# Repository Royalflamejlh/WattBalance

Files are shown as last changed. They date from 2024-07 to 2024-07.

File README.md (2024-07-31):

# ECE445-Wattbalance

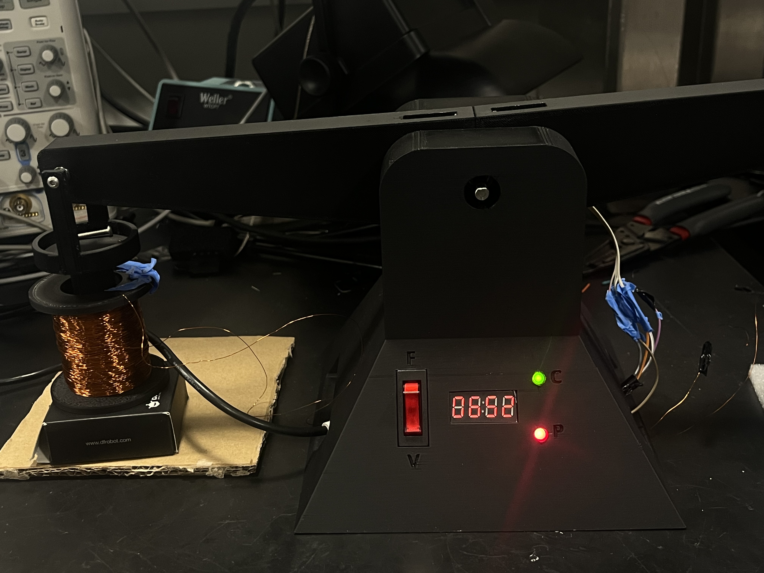
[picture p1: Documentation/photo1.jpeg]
Watt Balance


## Introduction
Our senior design project focused on the development of a Kibble balance, also known as a watt balance. This is an instrument capable of precise measurements based on electromagnetic forces and the definition of a kilogram based on fundamental constants. Our design is focused on the two main working modes of a watt balance, velocity mode in which a coil constant is calculated, and force mode in which that coil constant is used to realize some mass. We designed a custom 3D printed balance, along with a custom PCB to drive the measurements. Once assembled we found that velocity mode on our balance was inaccurate, but our force mode performed as expected. With a manual estimation of the coil constant, we were able to get accurate mass readings from our balance. The designs, failures, and successes are all documented in the following report.

## Features
- **Custom 3D Printed Balance**: Designed for precise measurements.
- **Custom PCB**: For accurate measurement and control.
- **Velocity Mode**: Calculates the coil constant.
- **Force Mode**: Uses the coil constant to measure mass accurately.
- **Manual Estimation**: Allows for accurate mass readings.

## Read More
For more detailed information view:
- [Proposal](Documentation/proposal2.pdf)
- [Design Document](Documentation/design_document1.pdf)
- [Final Presentation](Documentation/other1.pdf)
- [Final Report](Documentation/final.pdf)

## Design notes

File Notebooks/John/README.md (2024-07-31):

# Watt Balance

From the Project Proposal

>Since 1879, the universal standard of a kilogram was derived from a physical mass made of a platinum-iridium alloy stored away in a vault.  However, even with careful preservation in optimal conditions, over time the mass of the object drifted slightly, which is problematic for use as a constant standard.  In 2019, as part of a sweeping change to the SI system, the kilogram was redefined to depend on Planck’s constant rather than the mass of a physical object.  Researchers at the National Institute of Standards and Technology (NIST) developed a device called a Watt Balance (or Kibble Balance) that uses induced magnetic fields to precisely determine the mass of a given object by measuring the rotational velocity and force generated by the balance.  A group of graduate researchers in the ABE department of UIUC created a simple replica of this balance using LEGOs, but it is imprecise, often off by 20-30% or more on measurements.  This is problematic for a device whose goal is to create very precise measurements.

>Our solution for this problem involves iterating on the design created by the UIUC graduate researchers and creating a more precise and easier to use Watt Balance.  We plan to improve the sensing capabilities of the device and make mechanical improvements to help support those changes.  By replacing the 3d printed fulcrum of the balance with a smooth axle and bearing, we can not only reduce friction in the balance, but also use a more accurate sensor on the axle than the ultrasonic sensor the previous design used.  We plan to improve the sensing of the induced current in the coil using an ammeter rather than the arduino ports as it was previously measured to further increase the accuracy of the mass calculation.  We also plan to update their current MATLAB-based software implementation to a more powerful language to allow for more efficient processing of the data.

# Meeting Log

## 02/08/2024

### Understand the project and discuss project goals with the graduate researchers

During this meeting discussed the current state of the lego watt balance, and got an understand for the scope and expectations of the project.
We hope that with a custom PCB, and new sensors we can improve the accuracy to a level that the watt balance will be and acceptable scale to use.

## 02/16/24

### First Discussion with TA

During this discussion we mainly focused on our Project Proposal. We discussed places where points were lost and modification that should be made to the project proposal. The notes from the meeting include these points:

- Find a new 3rd High-level requirement that can be tested quantitatevly.
- Add metrics and error bounds to requirements.
- Redo the block diagram to be more descriptive of components.
- Add voltage regulator to diagram, we are not allowed to use 5v power supply, and need to have a somewhat more sophisticated power subsystem.
- Make lines thicker on block diagram to improve visibility.
- Start thinking about necessary components and ordering parts.
- Add references to external links and codes.
- Review similar projects safty guidelines to reconsider our own saftey guidelines.

## 02/22/24

### Second Discussion with TA

We discussed which current sensor to use and what are plans are going forward. We have a list of things we need to do going forward:

- Email grad students about power system
- Start designing PCB
- 1st Round PCB order prep
- Go to pcb way and upload check / audit by the tuesday before the order to check for errors
- Figure out the saftey portion of the design document
- Get an accurate range of masses that the balance can measure

### Finished Design Document

Finished and submitted the design document.

## 02/23/24

We updated the proposal to include:

- Better tolerance analysis
- References and citations

And we rewrote the saftey section.

## 03/04/24

### Part Selection Discussion

Discussion of which parts to get

Possible parts

- M9105-K12 (Position sensing)
- ERCK HE Sensor (Position sensing)
- ACS70331EESATR (Current Sensing)

also Justin and julian worked on figuring out how to do the cad sharing and started working on the physical modeling.

## 03/05/24

### Third Discussion with TA

Notes from the ta meeting:

- Need to get a better tolerance analysis
- Make is clearer how current is being used
- Make BLI equation and usage clear

also we got the instructions for how to use myECE

## 03/19/24

### Discussion with Team

No TA meeting, the board cad has been started, and the physcial cad model is mostly done with the prototype. Decided on ATMega chip and board parts.

## 03/24/24

Met in discord call to order parts. Ordered:

- ATMega328PB
- ERCK 05SPI 360
- USB4085
- FT232RL

and discussed the operations the pcb must perform, such as communication with a computer, driving the coils, reading the current sensor, reading the hall effect sensor and getting power.

We also have a list of things Justin is ordering for the mechanical:

- Bearing
- Coil wire
- USB cable
- shaft
- plastic
- magnets

## 03/25/24

Finished schematic and pushed the changes, julain completed the footprints and order placed.

## 03/27/24

Wrote and finished the individual progress report

## 03/31/24

Found issue in the ordering of parts, the status was not set to approved so we have to wait before we start are assembly, which we planned to do tommorow.

## 04/01/24

Setting up coding enviroment. For our chip the pb we have to use the atmel studio ide, looked into using vscode but had to custom change the include headers files to correctly compile for the pb.

## 04/09/24

Did not have TA meeting. We got our pcb delivered.

## 04/10/24

Orders have arrived and fixed issue with another order not going through, also found our pcb and screen in the room.

## 04/11/24

Soldered together PCB, we are missing crucial components so we stopped.

## 04/12/24

### New Schematic

Started redesigning the schematic with some big changes

- Way to deliver correct bipolar voltage to the atmega adc through a voltage shift
- Add a pwm controlled half bridge to send out the current
- Found a esd protection chip for the usb port
- Got new values for the oscillators
- Changes the usb chip we are using the the rtl
- set up the opamp to deliver bipolar power

## 04/13/24

### Finished schematic

Put finishing work on schematic and helped with the footprints

Also ordered all the new parts necessary for our new schematic, the op amp half bridge voltage power supply negative, and the esd protection

### Coding I

Set up and started working on the code in microchip studio
For the code I chose to write it in C

## 04/14/24

### Coding II

Adding libraries to the code that I find on github which are helpful for interfacing with the device. Spending lots of time writing the HAL layers for each chip to communicate the the mega. Right now have each mode be driven by a timer with a update callback function that does the respective stuff.

## 04/16/24

### Coding III

Finished up coding and reorganized code to make it look nice

### Mock Demo

For the mock demo we have the main part of the balance done, but nothing is operational as we dont have a pcb. Also our HE sensor might not work because the data sheet says its specified as a CW version.

## 04/18/24

### Soldering I

We started soldering the new pcb order, also got a list of all the parts not connecting.  We found that the current sensor was place in parallel not in series causing issues. Our esd chip is to small for our board. Also we were not able to find a short and ended up smoking our usb to uart chip.

## 04/20/24

### Soldering II

I went to the part shop and found a replacement usb chip, along with the missing components for our board. Also found we need to order another lm1117.

### Coding IV

Worked on testing and debugging code, tried to use a simulator but had to manually type the IO on pin, the arduino also cant take on the code.

## 04/21/24

### Soldering III

Picked up the parts from the supply center, we are having trouble now getting the atmega to program now that we have all the new parts.

We found that the ground for the chips was not connected in the footprint, and as a result we have to solder many jumper wires to many chips. Also found replacement op amp in self service. Also found the the self service had the same uart to usb chip that we are using so blowing it up wasn't a problem.

Gave up on getting atmega to work and wrote basic code on the arduino to drive the coil B so we have something to show for the demo

## 04/22/24

### Demo

The demo went well

## 04/23/24

Continued to work on seeing if the atmega could program, but it seems there is no way to communicate with the chip. We have decided to just use the arduino uno for the rest of the project.

Helped write the slides for mock presentation.

## 04/24/24

### Mock Presentation

Went, got the feedback:

- Less text on the slides
- r&v tables
- Talk like proud of project
- Hand placement (not in pocket)

## 04/25/24

Wrote code to iterate through all the possible spi values to hopefully get a reading from the hall effect sensor

## 04/26/24

Got the SPI reading from the sensor and started getting the rest of the calculations to work

Wrote a bunch of slides for the next presentation and started getting visual for it

## 04/27/24

Met today to work more on code and balance, pretty much everything is working, it just is not very accurate, as the BL is wrong.

## 04/28/24

Met today and got data from the balance by forcing it to print all the reading in each mode. Also got oscilliscope readings for the presentation and for the slides. 

## 04/29/24

Kept working on the slide show and added all the graphs and readings into the slides show and reordered the slide show to flow correctly.

## 04/30/24

### Presentation

Our presentation went well and the ABE team to watch it.

### Final Report

Started on the final report, I organized it and wrote the 1st section (introduction) today, as well as the pcb part of the design while justin wrote the mechanical portions

## 05/1/24

Finished the final report today, created the references and wrote the design verifications for the non mechanical subsystems.

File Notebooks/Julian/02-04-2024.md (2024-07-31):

# Indicator for Carbon Emissions

## Phase 1

- Power
- WiFi
  - API connection
- Process data
- LED control
- Sound (maybe)
- Button input (maybe)

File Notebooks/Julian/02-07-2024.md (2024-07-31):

# Watt Balance

- measures mass of an object using constants instead of comparing against a known weight
- 2 modes, force and velocity
- force mode measures current
- velocity mode measures voltage and velocity

## Current Grad Team Watt Balance

- 20-30% accuracy
- takes a while to calculate mass
- using arduino and external power supply
- ultrasonic sensor for position
- controlled with matlab
- grad team has the balance move the coils, told us we should move the magnets instead

## Key Objectives

- Custom software to control the watt balance
  - communication between computer and balance
  - calculations done on microcontroller, calibration done with software
  - simple display on balance to show calculated mass
- Custom pcb
  - Microcontroller
  - USB connection to computer
  - Drive coils, calculate mass
  - PID system to balance the scale
- Physical Balance
  - 3D-Print instead of LEGO
  - Replace ultrasonic sensor and fulcrum with Hall effect sensor and axle and bearing

[NIST LEGO Watt Balance Video](https://www.nist.gov/si-redefinition/nist-do-it-yourself-kibble-balance-made-legor-bricks)

[NIST LEGO Watt Balance Paper](https://pubs.aip.org/aapt/ajp/article/83/11/913/1039505/A-LEGO-Watt-balance-An-apparatus-to-determine-a)

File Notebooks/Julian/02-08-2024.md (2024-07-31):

# Planning the watt balance

## Subsystems

### Power

- DC to AC convertor for coils
- Power the pcb

### Measurement

- Calculations done on pcb
- control loop/ calibration
- Ammeter for coil current, Hall effect sensor for rotation

### Mechanical

- Hall effect sensor with an axle should have little friction
- electronic shielding?

### IO/Data

- communicate with computer if connected
- use to calibrate or change settings
- calculate velocity from change in angle
- use voltage and velocity to get coil constant
- use current and coil constant to get mass

## Equations

- Force mode

$F = ma = BLI$

- Velocity mode

$V = BLv$

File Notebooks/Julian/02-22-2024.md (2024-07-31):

# TA Meeting 2 and design doc

- improved visual aid
- error percentage addad to requirements
- added verifications
  - use oscilloscope to measure current and voltage
  - use protractor to measure angle
  - use known mass to verify scale works
- talk about safety

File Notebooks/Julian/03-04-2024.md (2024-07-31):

# Team meeting

- set up gitlab for pcb and balance
- Decided on some parts

[Hall Effect Sensor](https://p3america.com/erck-05spi-360/)

[Current Sensor](https://www.digikey.com/en/products/detail/allegro-microsystems/ACS70331EESATR-2P5U3/8120683)

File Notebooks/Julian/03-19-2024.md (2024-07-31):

# Started work on pcb

- basic schematic for programming atmega328p
- connections for Hall effect sensor, spi programming, USB-C port, current sensor

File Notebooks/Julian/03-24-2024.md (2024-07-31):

# Team Meeting

- Finalised parts list
  - decided on ATmega328PB for microcontroller
  - found USB-UART chip
  - 3d printer filament
  - copper wire, magnets

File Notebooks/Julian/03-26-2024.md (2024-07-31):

# Finishing PCB

- ATmega328PB footprint added
- Footprints for resistors, diodes, capacitors added
- Using random footprint for Hall effect sensor, no dedicated footprint
- footprint for 5v to 3.3v voltage regulator and current sensor
- pcb passed audit, submitted for PCB wave 3

## PCB Layout V1

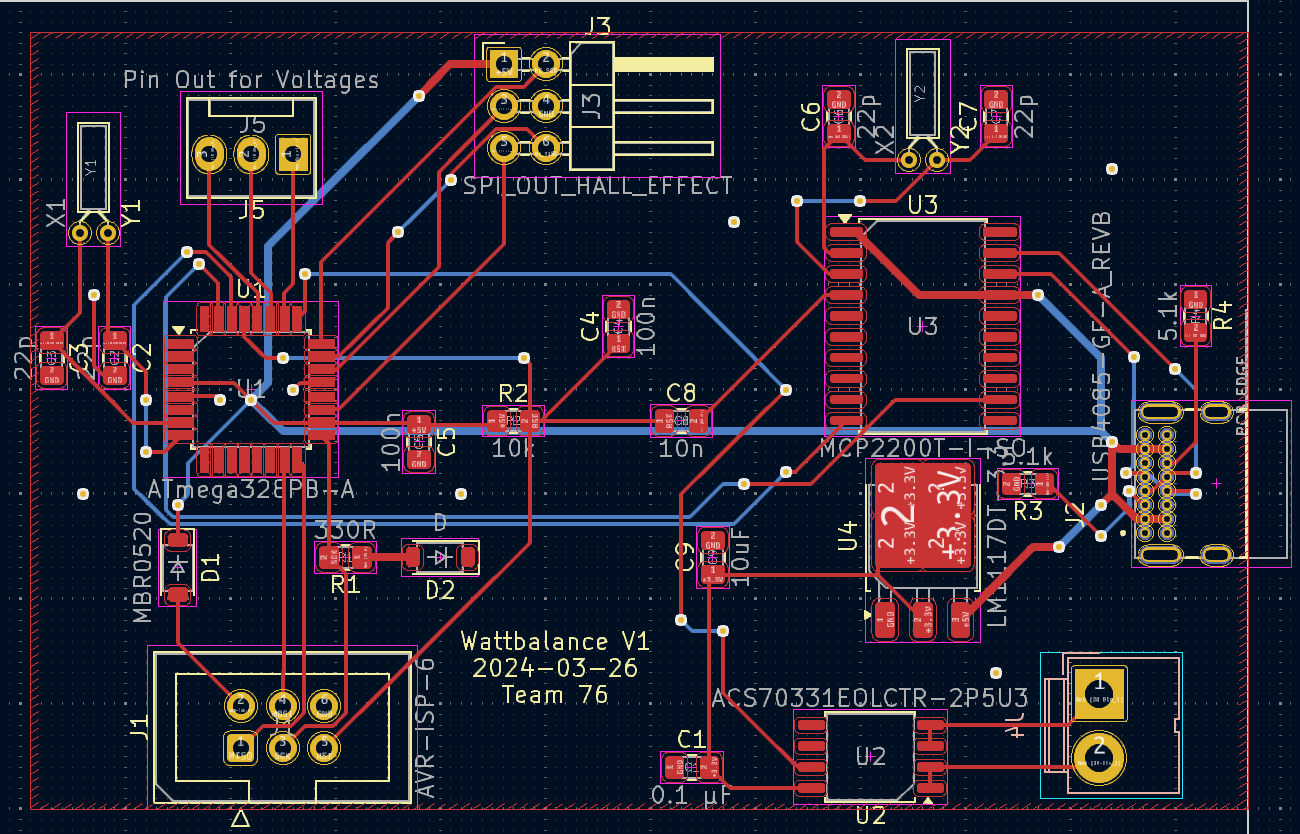
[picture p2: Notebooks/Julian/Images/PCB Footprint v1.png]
PCB Layout Version 1


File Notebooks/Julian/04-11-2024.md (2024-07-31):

# Team meeting to work on the board

- a few parts were missing from the schematic, some of the footprints were wrong
- plan to update schematic and correct footprints by end of week, so we can order a new pcb quickly

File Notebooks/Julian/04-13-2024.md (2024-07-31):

# Working on PCB Layout V2

- corrected footprint for the oscillators, only one now
- H bridge was added to schematic, found footprint
- Added more footprints for molex connectors for coils and voltage checking
- Placed footprints for GPIO headers, OPAMP, DAC, LEDs
- Changed Hall effect sensor footprint to ISP connector because it's similar

## PCB Layout V2

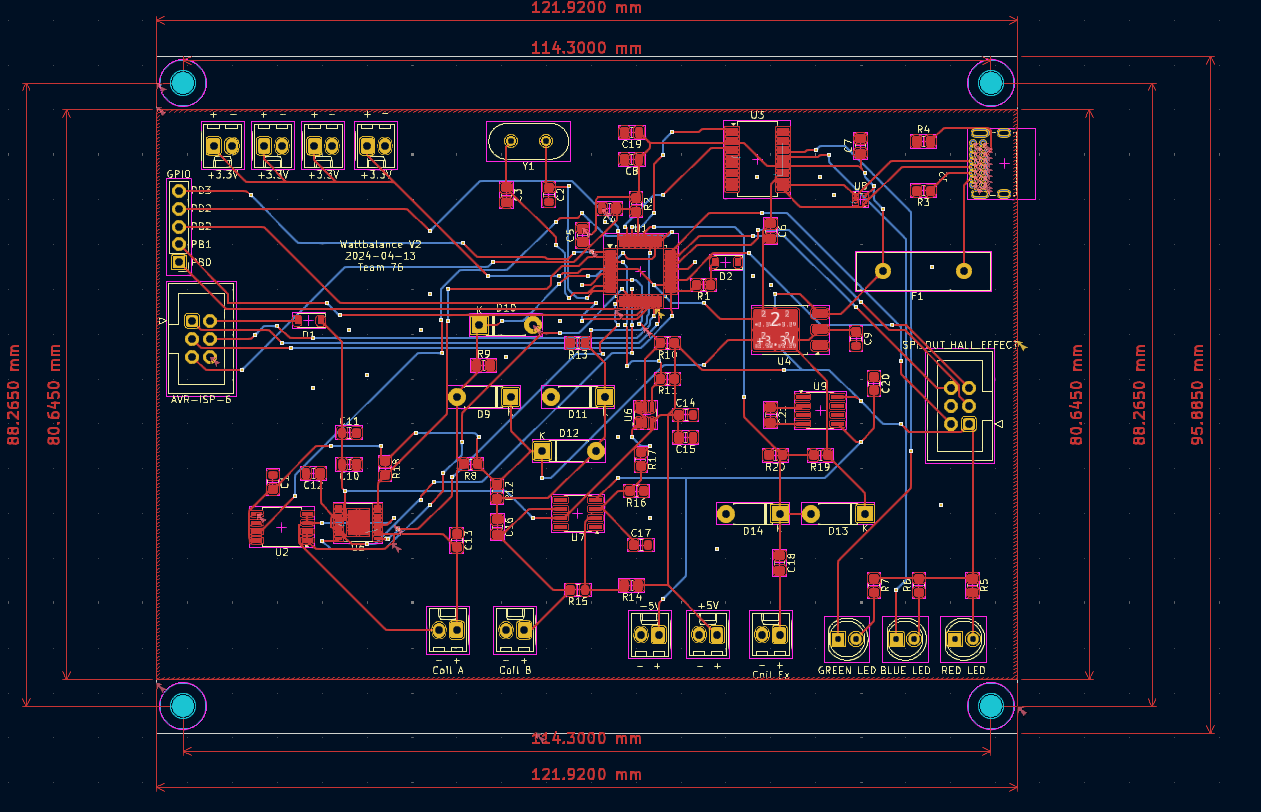
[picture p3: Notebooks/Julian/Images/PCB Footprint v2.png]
PCB Layout V2


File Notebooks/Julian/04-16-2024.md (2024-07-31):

# Mock Demo

- Physical balance is designed and printed
- Still waiting on 2nd pcb
- Start the coding

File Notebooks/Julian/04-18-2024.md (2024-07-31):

# Soldering Day 1

- PCBs arrive, soldering begins
- Missing a few parts
  - Mainly capacitors, resistors, and diodes
  - Need to get a fuse, LEDs
  - Wrong OPAMP footprint for the package we got, ordering the correct one
  - Esd chip is very small
  - Placed an order for the 3.3 to 5v voltage regulator
- Some grounding missing on H-bridge

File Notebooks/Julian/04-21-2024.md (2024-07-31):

# Soldering Day 2

- Discovered missing grounding on USB-UART chip, had to add jumper wires
  - This resulted in us shorting the board, luckily we had a fuse to protect the components
  - We figured out it was the issue when we pushed 3Amps through the board and fried the chip
  - plan to get new UART chip tomorrow from ECE Parts shop

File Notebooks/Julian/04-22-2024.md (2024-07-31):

# Soldering Day 3

- UART chip is soldered onto board, there are no shorts
- Unable to program atmega for some reason
- Last minute switch to arduino
  - Have to write new code using arduino IDE
  - Velocity mode works, but we dont have fine control over the voltage applied
  - Cant get hall effect sensor to work

## Board accepts power with no shorts

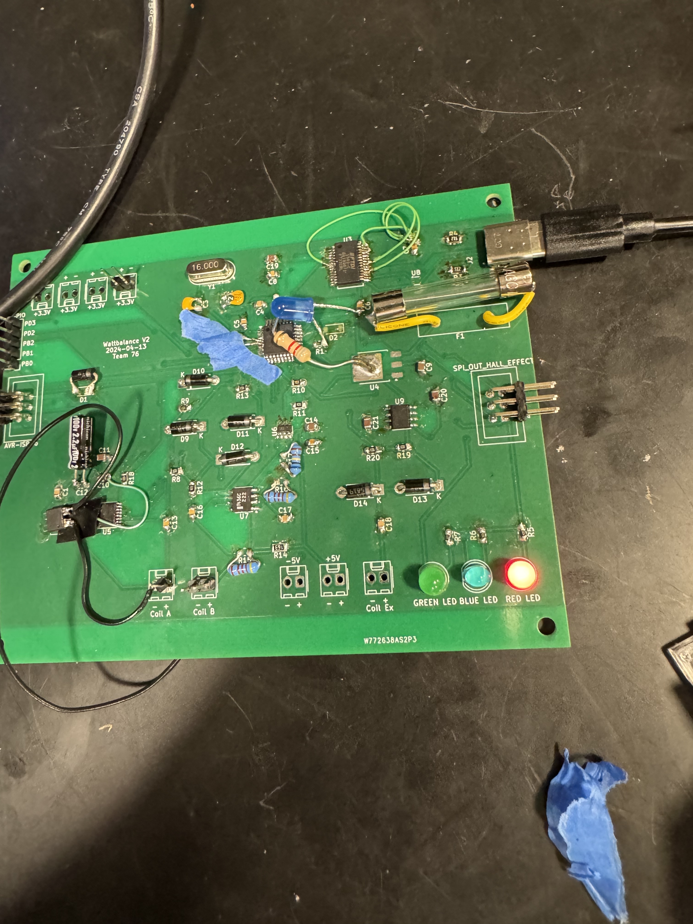
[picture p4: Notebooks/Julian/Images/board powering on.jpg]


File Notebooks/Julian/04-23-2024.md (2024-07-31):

# Final Demo

- Velocity mode is working, hall effect sensor does not
  - LEDs, display working, but theres nothing to display bc force mode doesnt work yet

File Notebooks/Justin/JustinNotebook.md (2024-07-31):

# 2024-02-07
Today we met with the graduate student team from the ABE department who pitched our project.  They showed us their balance and gave us a demonstration of how it worked, as well as talked a bit about the physics and calculations behind it.  They also pointed us to a helpful reference that they used to build their project, the original NIST paper, which I believe will be very helpful in the design and creation of our device
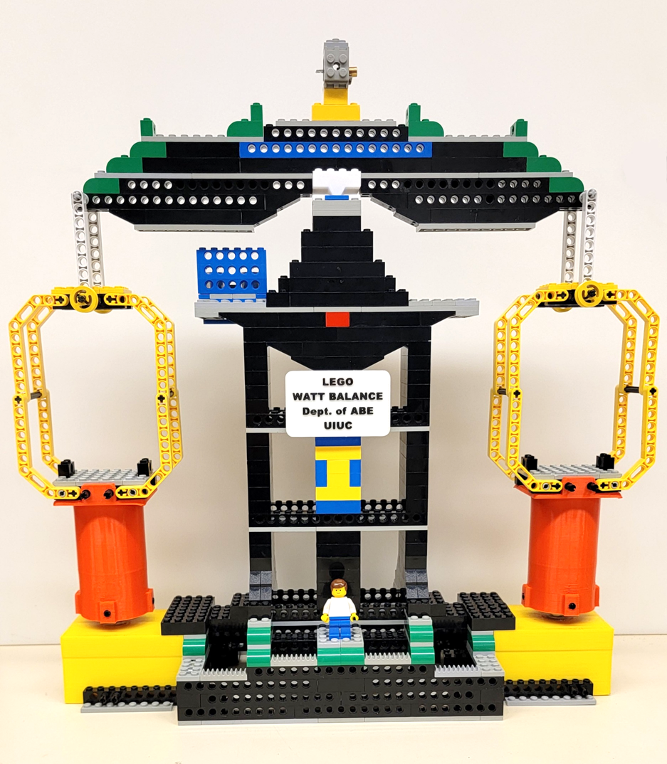
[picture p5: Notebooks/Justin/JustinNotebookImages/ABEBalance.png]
The ABE department's Watt Balance

I created a GitLab repository so we could store all of our notebooks and future code and design information
We also started working on our proposal, as the deadline is already fast approaching.
# 2024-02-08
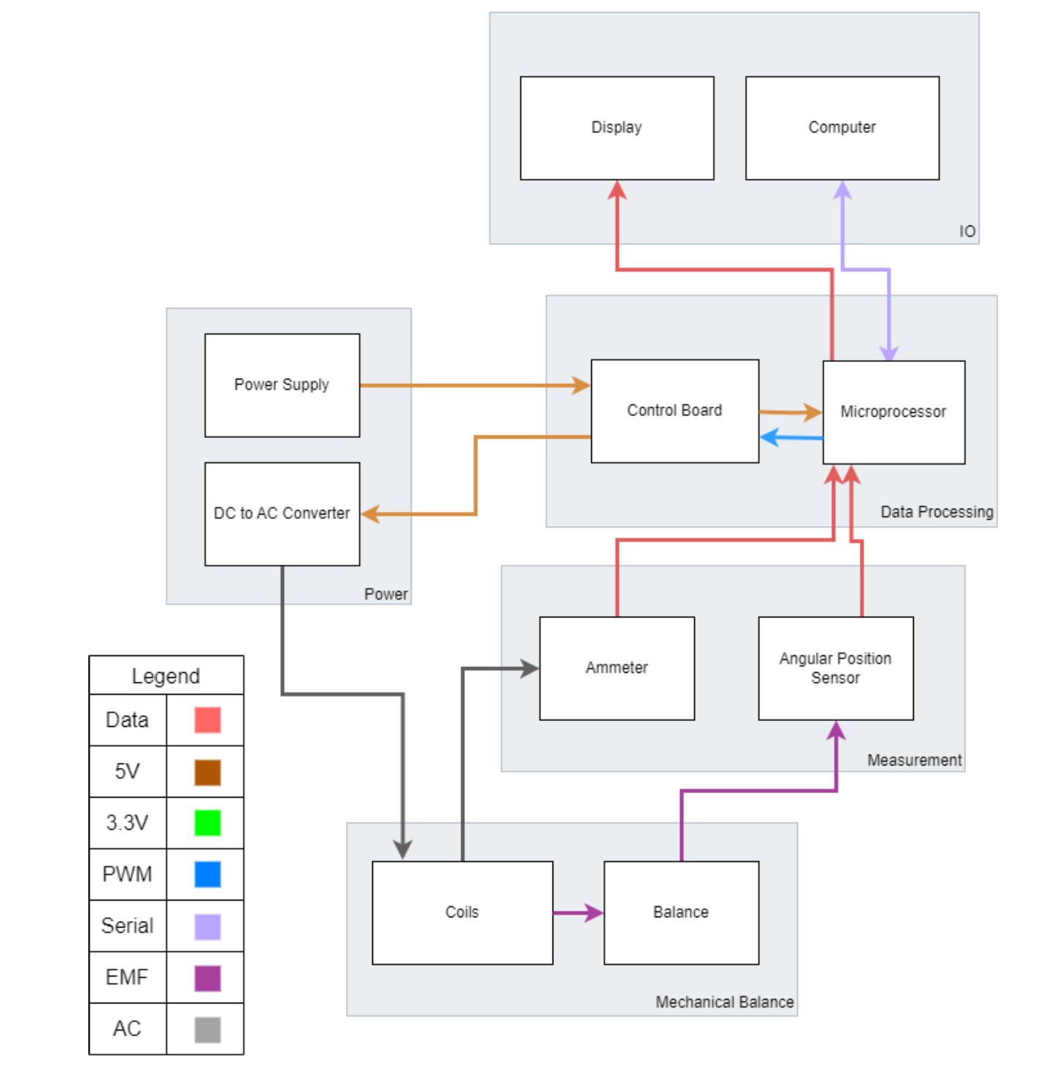
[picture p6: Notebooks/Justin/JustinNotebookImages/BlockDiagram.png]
Block Diagram
Today we all worked on the proposal and got it finished up in time to submit to the web board before the deadline.  We also finished up our RFA and submitted it to the web board.  Additionally, we also filled out our team contract.  Even though none of us know each other going into the project, I think we will work well as a team.  We also created a block diagram to go in our proposal document 
# 2024-02-15
Today we met with the TA for the first time.  She helped give us a bit more background about the project and what it entails.  She also gave us some feedback about things we needed to change on our proposal document, and said that we can resubmit it next week for some points back
# 2024-02-22
We haven't done much work in the last week, but today we started on the design document to get that started, and also did a bit more work on the proposal revision.  Because the gravitational constant is a key part of our calculations, I also did some research on what the local gravitational constant is in Champaign, as it can vary sligtly from place to place, but the best I could find was some [measurements from the 1980s](https://van.physics.illinois.edu/ask/listing/223), which should still be roughly accurate today.  
# 2024-03-04
Today we had a big meeting to pick all the different components we would use in the project.  I was in charge of finding the Hall effect sensor we would use for angular position measurements, and I found [this sensor](https://p3america.com/erck-05spi-360/), which I believe should work well for our purposes
# 2024-03-05
Today I started on the CAD design of the balance, which will be my main goal on the project for a little bit, as it is something that I have experience with that my teammates do not.  So far, this is what I have in the design:
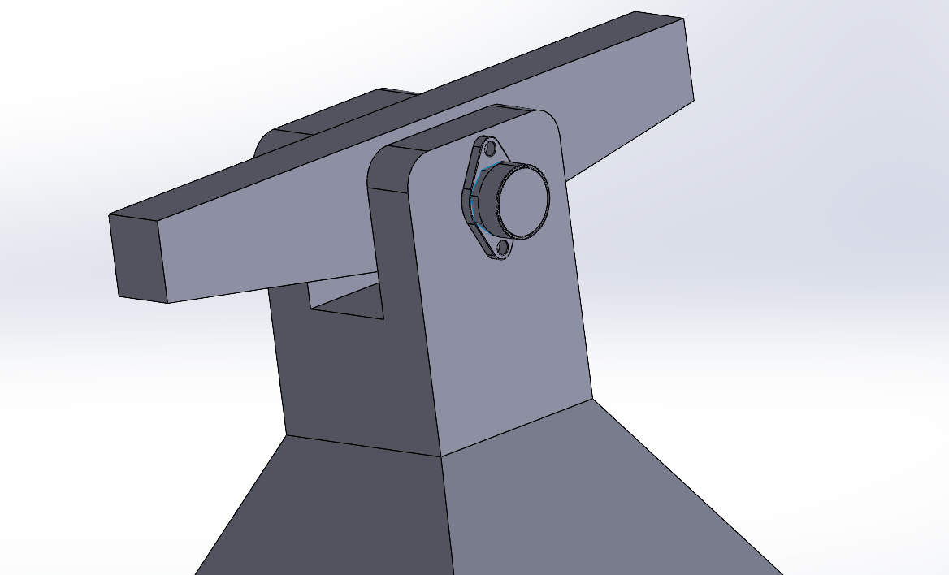
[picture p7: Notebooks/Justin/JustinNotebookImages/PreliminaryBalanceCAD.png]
Preliminary Balance CAD

The dimensions are somewhat temporary until we do a bit more work on the design side to figure out what they should be, but I am quite happy with the general shape.  Fortunately, the Hall effect sensor has a CAD model on its website, so I don't have to make one myself.
# 2024-03-17
I've done some more work on the CAD to try to get it into a more completed state.  Some of the changes include
- Making the baskets
- Getting more finalized dimensions
- Planning for 3d printability
- Creating hooks to mount the baskets on

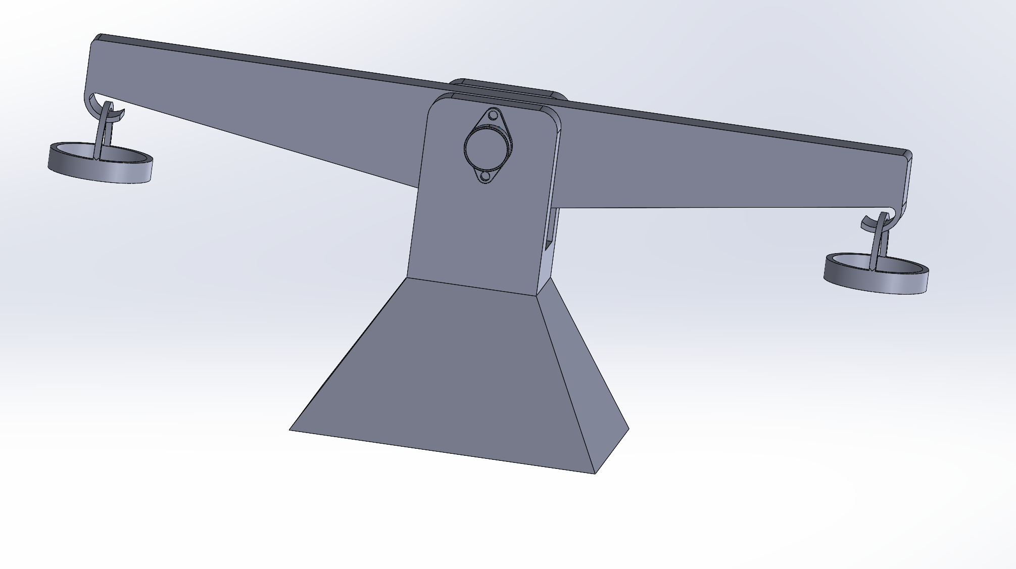
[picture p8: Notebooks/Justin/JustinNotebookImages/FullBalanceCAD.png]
Full Balance CAD

I also modeled out a bit of the motion path of the balance as it swings, and I believe we should be alright with setting fixed coils below the buckets
# 2024-03-24
Today we finalized all of the parts we plan to use in the project and placed the order.  I found this [USB to UART](https://www.mouser.com/c/semiconductors/interface-ics/usb-interface-ic/?standard=USB%202.0&type=Bridge%2C%20USB%20to%20UART) IC that should work nicely for our purposes, as well as some [magnet wire](https://a.co/d/4URU0I1) and [magnets](https://a.co/d/9Svq8fp).  Here is a list of everything we need for the project:
Physical needs:
- Bearings
- Wire for coils
- USB-C cable
- Shaft(s) (and maybe collars)
- Plastic for printing
- Magnets

Electronics Needs:
- Microprocessor
- USB-C jack
- Current Sensor
- Hall Effect Potentiometer
- Resistors, capacitors, etc
- Wire
- 7 segment display
- Usb to uart

# 2024-03-26
Today I didn't do much work on the balance, but I did order some of the additional components we need, like bearings, a shaft, and some extra magnet wire in case we need more

# 2024-03-27
Today I finished up my individual progress report.  It is quite long, and contains a lot of the information from previous notebook entries.

# 2024-04-10
Today, our PCBs finally arrived.  We have been waiting a long time for them, but we should now be ready to start soldering and assembling
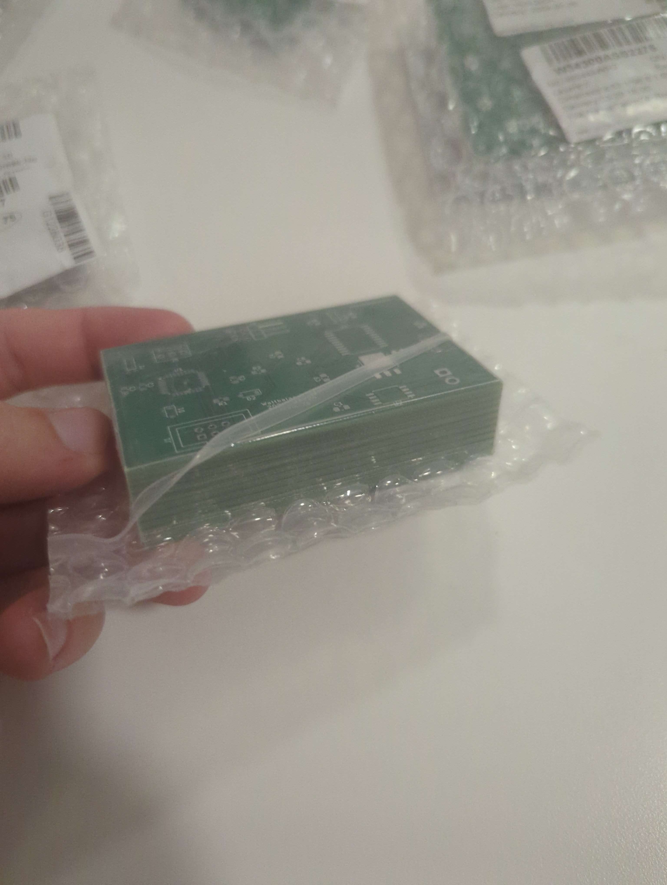
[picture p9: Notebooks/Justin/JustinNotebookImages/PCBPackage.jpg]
Our PCBs


# 2024-04-16
Over the past few days, I have been printing out the parts for our balance, and I have now assembled all of them to test out how the motion works.  It swings super smoothly, the bearing is great!
The Balance
I also decided that 8 of the second largest size of magnets on each side should be good to have the strength and size ratio we want

# 2024-04-18
Today I unwound the magnet wire from the spool it came on and wound it onto some custom spool holders I printed that should be the right size for our purposes.  It took quite a while, as there are several hundred windings, but I eventually got it done.  I am glad we decided to get a spare spool of wire just in case, because each holder takes a full spool of wire, so we wouldn't have had enough otherwise
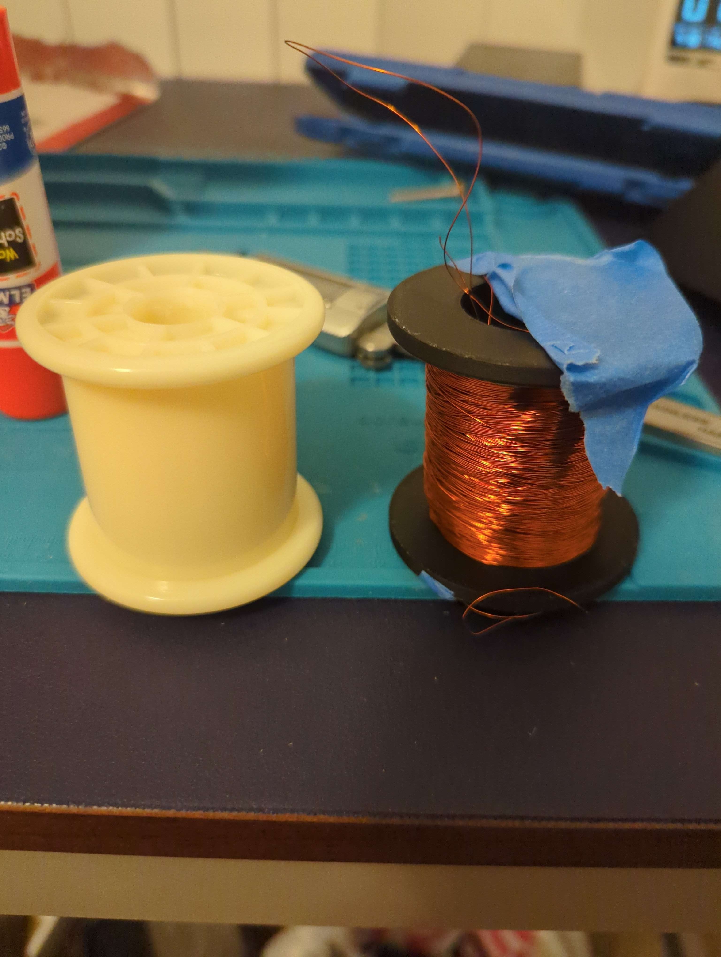
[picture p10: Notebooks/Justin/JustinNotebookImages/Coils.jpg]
The Wire Spool

I also soldered everything onto our PCB except for a few components that are still yet to arrive.  It is looking good!

# 2024-04-19
Today I soldered a bunch of stuff onto the new PCB we designed that should work much better than the old one.  We accidentally made a mistake in the PCB design though and put the current sensor in parallel, not series, so I had to make a few modifications with jumper wires
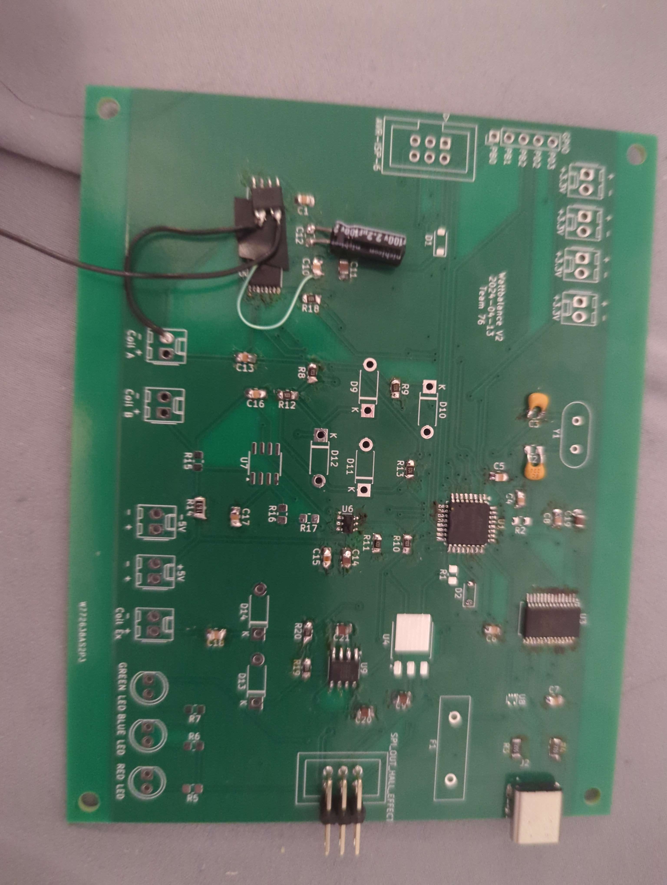
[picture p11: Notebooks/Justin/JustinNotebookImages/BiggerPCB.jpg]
The Larger PCB


# 2024-04-20
Today I soldered on some more of the components that we got including a fuse.  We didn't have a fuse holder though, so I eventually just wound up soldering the two ends of the fuse directly to some wires.  It may not be easy to replace, but hopefully it should still work
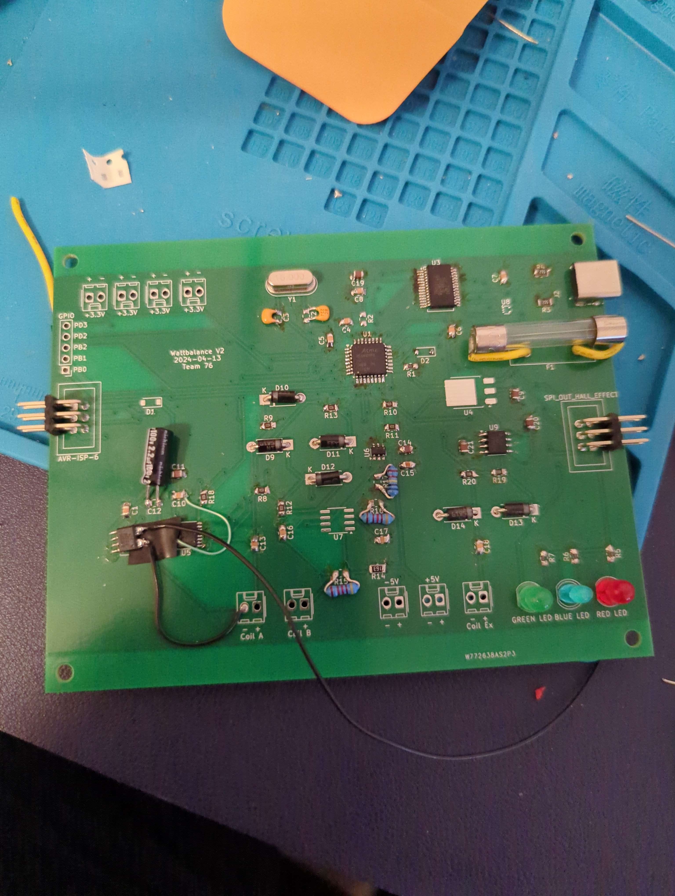
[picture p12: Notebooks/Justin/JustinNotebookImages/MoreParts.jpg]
The updated PCB


# 2024-04-21
Today I finished a major redesign of the base of the balance to house the larger PCB.  I also spent a lot of time making cutouts for our front IO, which required a lot of iterations of tests to get to fit just right, but I eventually got it
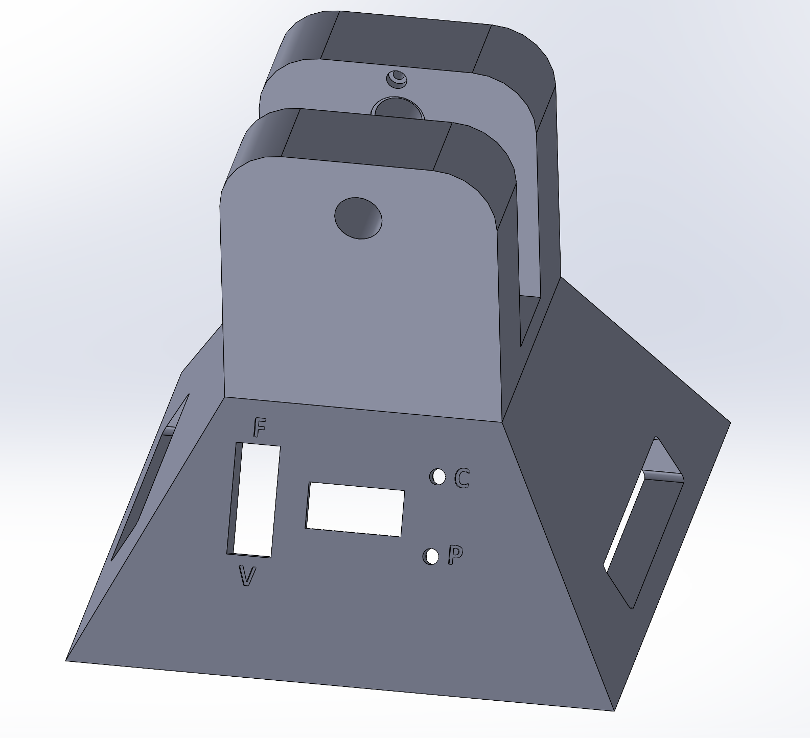
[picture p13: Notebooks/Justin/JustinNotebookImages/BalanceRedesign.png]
The redesigned base

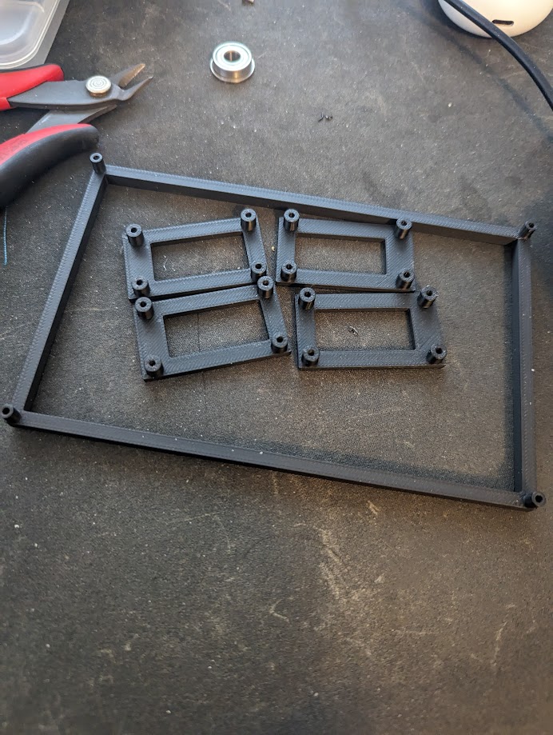
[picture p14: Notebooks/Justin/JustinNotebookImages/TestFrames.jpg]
The test parts

It is printing out right now, so hopefully it works, as I am using up the last of the printer filament we have.

The print just finished, and it looks great!  The front io fits super well
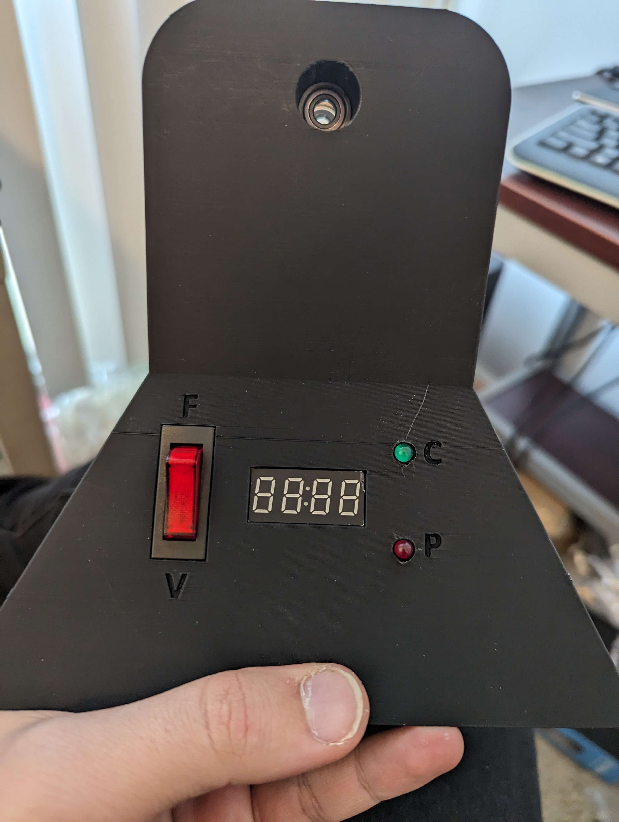
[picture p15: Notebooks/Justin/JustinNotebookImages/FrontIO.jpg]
Front IO


# 2024-04-26
Today I took some test data from the position sensor now that we finally have it working (after our demo unfortunately).  We had a lot of problems getting the SPI interface to work, since it is non standard and not very well documented, but we eventually iterated through every possible combination of settings until we found one that works.  Here is what the data looks like, it is quite smooth!
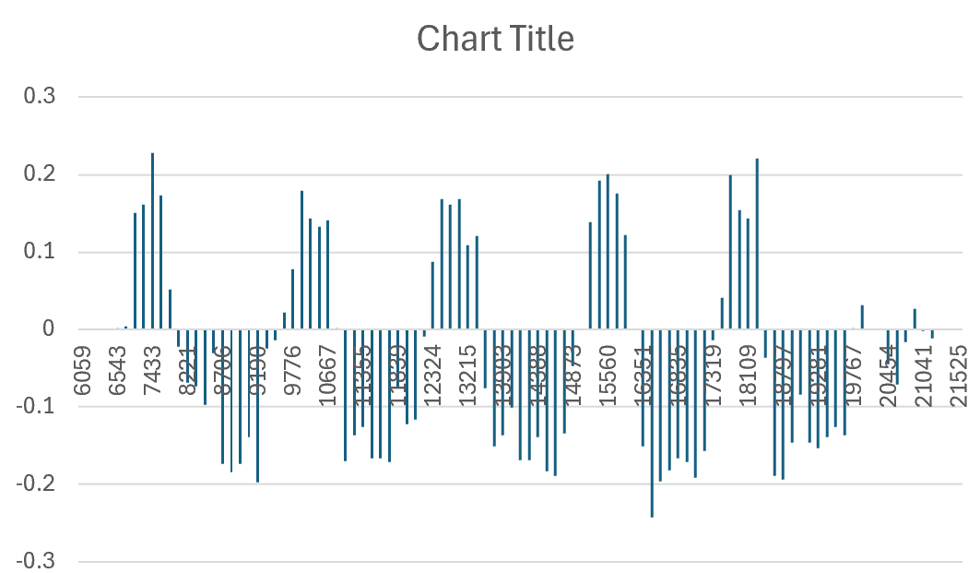
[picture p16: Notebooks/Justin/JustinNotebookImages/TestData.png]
Position Data


# 2024-04-28
After our data collection session today, I made a bunch of graphs of the data to include in our presentation and final report, like these two.  I think they came out well!

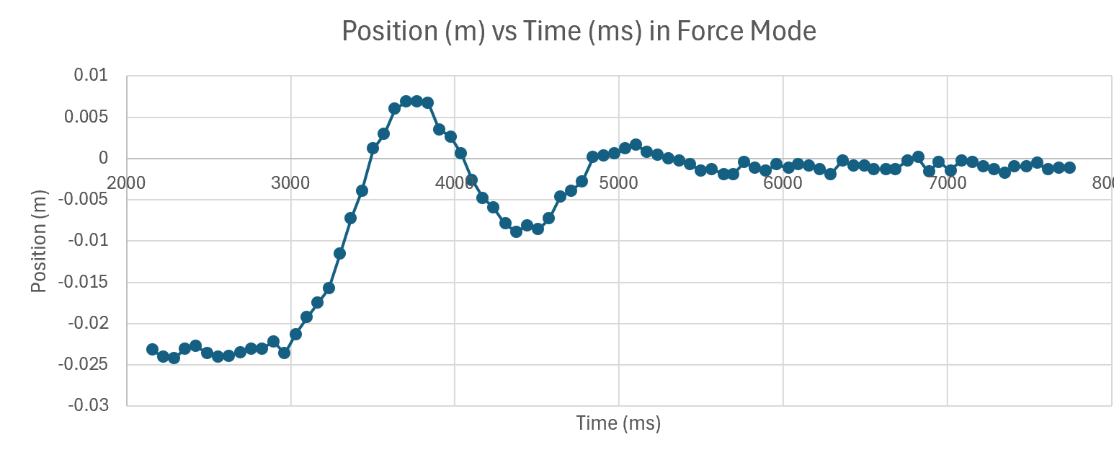
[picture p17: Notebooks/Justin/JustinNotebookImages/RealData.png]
Graph 1

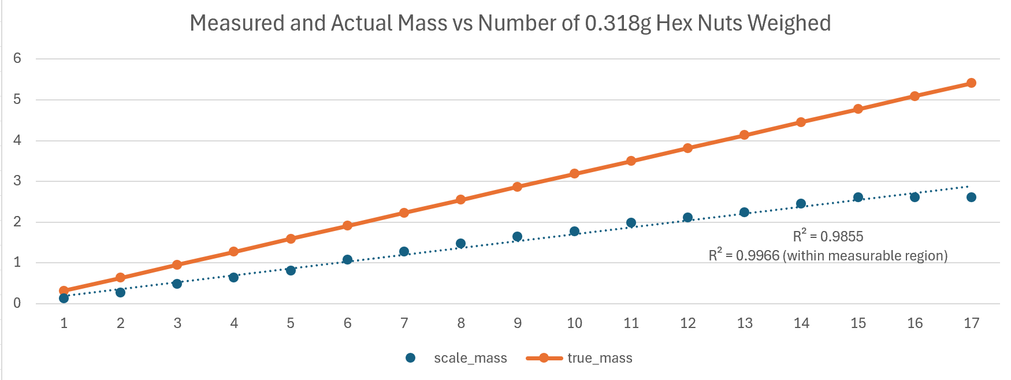
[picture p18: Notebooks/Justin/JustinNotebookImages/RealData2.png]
Graph 2

The rest are in our presentation!

# 2024-04-28
Today we gave our presentation, and while we weren't able to collect all the data we wanted due to having to switch to the Arduino, it still went pretty well.  We invited the graduate team from the ABE department that pitched the project in the first place, and they seemed quite impressed!

# 2024-05-01
Today we finished up the last part of our project, the final report.  Overall, I was quite happy with this project even if there were some areas that could be improved!

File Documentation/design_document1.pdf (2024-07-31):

# Watt Balance

## Design Document ECE 445

## Team 76

### Justin Ansell Julian O’Hern John Howard

### TA: Abhisheka Sekar

Introduction

Problem
Since 1879, the universal standard of a kilogram was derived from a physical mass made of a platinum-iridium alloy stored away in a vault. However, even with careful preservation in optimal conditions, over time the mass of the object drifted slightly, which is problematic for use as a constant standard. In 2019, as part of a sweeping change to the SI system, the kilogram was redefined to depend on Planck’s constant rather than the mass of a physical object. Researchers at the National Institute of Standards and Technology (NIST) developed a device called a Watt Balance (or Kibble Balance) that uses induced magnetic fields to precisely determine the mass of a given object by measuring the rotational velocity and force generated by the balance. A group of graduate researchers in the ABE department of UIUC created a simple replica of this balance using LEGOs, but it is imprecise, often off by 20-30% or more on measurements. This is problematic for a device whose goal is to create very precise measurements.

Solution
Our solution for this problem involves iterating on the design created by the UIUC graduate researchers and creating a more precise and easier to use Watt Balance. We plan to improve the sensing capabilities of the device and make mechanical improvements to help support those changes. By replacing the 3d printed fulcrum of the balance with a smooth axle and bearing, we can not only reduce friction in the balance, but also use a more accurate sensor on the axle than the ultrasonic sensor the previous design used. We plan to improve the sensing of the induced current in the coil using a discrete current sensor rather than the arduino ports as it was previously measured to further increase the accuracy of the mass calculation. We also plan to update their current MATLAB-based software implementation to a more powerful language to allow for more efficient processing of the data, and create an easier to use user interface to match.

Visual Aid

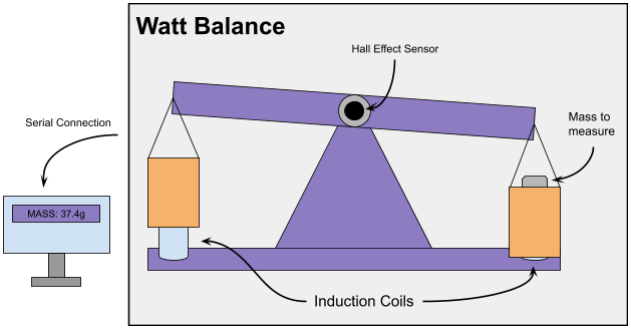
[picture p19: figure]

The Watt Balance works much like a regular balance scale, except instead of comparing against a known mass, the watt balance uses the current induced in the coils and the rotational velocity to compute the mass of the object. The Watt balance uses two modes, “Force” mode and “Velocity” mode. In force mode, the unknown mass is placed on one of the scales, and a current is applied to the coil such that the force applied cancels out the weight of the mass. In velocity mode, we apply a varying current to one coil, while measuring the resulting voltage in the other coil and measuring the velocity of the rotation. Using these measurements, we can solve the two equations ma = BLI and V = BLv for the mass of the object.

High-level requirements
- The device must be able to accurately measure the rotational velocity of the balance. Given that the error when using a known mass in the original ABE device was between 20-30%, we are targeting ~5% error for our measurements to be considered accurate, and ~1% error as a stretch goal.
- The device must be able to accurately measure the force generated by induction in the coil. Similar to the rotational velocity, we are targeting ~5% error for our measurements to be considered accurate, and ~1% error as a stretch goal.
- The device must be able to communicate with the control software and accept input calibration parameters given by the user of the device.

### Design

Block Diagram

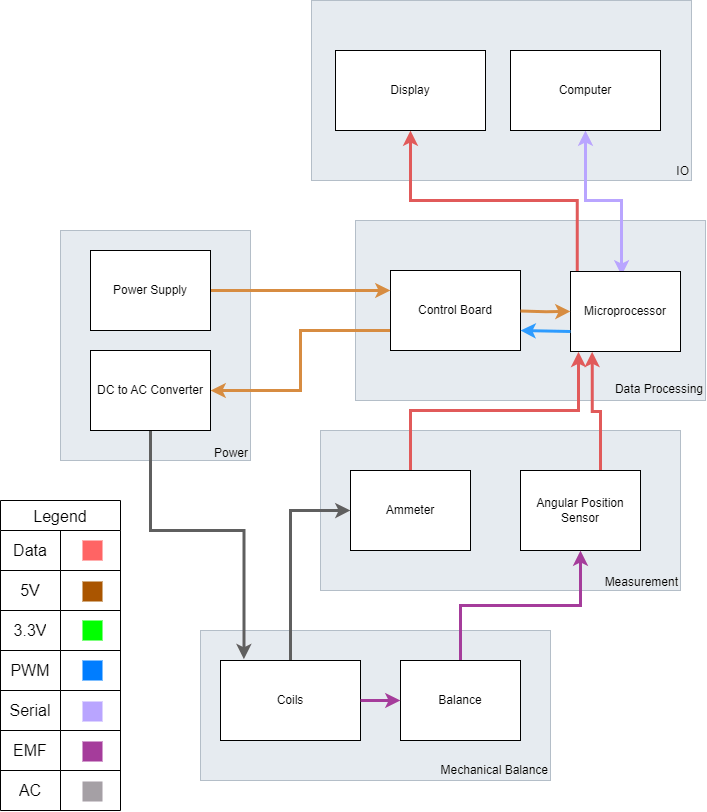
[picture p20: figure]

Physical Design
As of right now there are no physical modeling / designs with accurate measurements.

Device Subsystems

Power Subsystem

The power subsystem is the main source of power for all of the electronics, delivering DC power that is propagated throughout the entire device. The power subsystem also delivers a consistent and expected AC power to the coils to drive the balance force, and can be adjusted by the control board. This is important as precision in the input voltage is directly necessary to getting an accurate current reading from the ammeter.

Requirement | Verification
DC to AC converter (inverter) to the power coils. | Use an oscilloscope on the waveform sent to the coils to make sure they are consistent, and the desired waveform.
5v to the control board from the power supply. | Prob the voltage out of the power supply to make sure the voltage is correct and will not damage the components.

Measurement Subsystem

The measurement subsystems should both be able to measure the current induced in the coils, along with the movement and velocity of the balance as power is applied. The data from these measurements will be sent to the control board for both feedback and tuning purposes, and for calculating the mass of the object.

Requirement | Verification
Accurate sensing of angular position to within 5% error. | Begin with the balance at 0 degrees, then place a heavy object in the measurement area to ensure that it rotates as far as it can go. Compare the difference between the two measured values of the position sensor to the known maximum travel distance and see whether it is within 5% error.
Accurate sensing of current to within 5% error. | To verify, place the leads of an oscilloscope across the current sensor, then run the measurement program. Measure the current using the oscilloscope and make sure it matches with the measured value to within 5% error.

Mechanical Subsystem

The mechanical subsystem allows manipulation of the balance through the electromagnetic force generated by the coils. It also encapsulates the changes to the fulcrum of the balance to allow its angular position to be read by the angular position sensor

Requirement | Verification
Ability to move the balance using the force from an induced magnetic field in the coil | To verify, apply varying currents to one coil, and observe whether the balance moves as a result. Repeat with the other coil to make sure both coils are capable of moving the balance.
Minimal interference with other | To verify, use a gaussmeter to measure the

electronic components (shielding if necessary) | emf at the coils and an ammeter to measure the induced current. When each electrical system is activated (apart from the inverter) measure the EMF and the induced current to be sure that no interference exists.
The device must have minimal friction in the pivot such that a 10 gram weight is measurable to within the 5% accuracy tolerance. | To verify, place a known 10 gram object on the measurement side of the balance. Then, run the force and velocity measurements on the balance using the control software and see if the calculated mass value displayed is within 5% of the known mass.

Data Processing Subsystem

The data processing system should be able to take in input’s from the IO, sensors, and voltage readings, and correctly allow for adjusting parameters along with calculate and output measurements.

Requirement | Verification
Read in measurements from position and current sensors | To verify, run the measurement program and check that the measurements from both the position and current sensors are displayed in the control program.
Convert position and current data into angular velocity and force data | To verify, run the measurement program and check that the calculated values displayed in the control program match up with those calculated by hand given the measurements from the sensors.

Calculate the mass of the object based off the angular velocity and force data

To verify, run the measurement program and check that the calculated mass displayed in the control program matches with the value calculated by hand given the measurements from the sensors.

IO Subsystem

The IO subsystem will be the primary way for interacting with the control board, there will be some sort of display to give out reading from the sensors, and the mass, along with input methods to tune the inputs to the balance, such as voltage, and tune how the sensors are read.

Requirement | Verification
User interface software to input control parameters for the balance | To verify user input of parameters, run the measurement program once using the control program. Then, edit the configuration values in the control program. Finally, run the measurement program again and see if the resulting measurements have changed from their original values based on the new tuning parameters.
Display to read out the mass of the object on the balance | To verify the display of data, run the measurement program using the control program, then check both the control software and the LED screen to confirm that they both display the same measured mass

Tolerance Analysis

One critical component of the device is the rotational position measurement. Looking at Hall effect sensors, which are our current frontrunners for a positional sensor, many seem to be accurate to about 0.3%. Converting the position to velocity is a derivative relationship, meaning that the error in the measurement should remain as 0.3%, which satisfies our target threshold for the velocity measurement. We also will be averaging the slope across many points to further increase the accuracy of the measurement.

Cost Analysis

Physical Part | Unit Cost | Quantity | Subtotal Cost
Hall Effect Sensor | $35.00 | 1 | $35.00
Current Sensor | $1.57 | 1 | $1.57
LED Screen | $3.50 | 1 | $3.50
PLA filament | $20.00 | 1 | $20.00 Subtotal: $60.07
Labor Type | Number of Workers | Hourly Cost | Total Hours | Subtotal Cost
ECE Students | 3 | $50 | 8hr* x 15 weeks | $18,000
Subtotal: $18,000
The total cost after combining the cost of the physical parts and labor is $18,060.07

# Schedule

Week | Goals | Team Members
2/19 | Fix and submit Proposal for Regrade | Everyone

| Complete and Submit Design Document | Everyone
2/26 | Design Review Make revisions to design document Design PCB PCB Review | Everyone Everyone Everyone Everyone
3/4 | Teamwork Evaluation PCB revisions | Individual Everyone
3/11 | Spring Break
3/18 | Start to design software to work with new PCB and sensors Start to construct and iterate designs of balance | Julian John, Justin
3/25 | Test to make sure balance fits within expected tolerances Revisions to Software Revisions to Balance | John, Justin Julian John, Justin
4/1 | Make sure the balance and software interact correctly Revisions to Software Revisions to Balance | Everyone Julian John, Justin
4/8 | Small refinements and tuning to the final version of the balance. Make sure software is stable and accurate. | John, Justin Julian
4/15 | Mock Demo | Everyone
4/22 | Final Demo | Everyone

| Mock Presentation | Everyone
4/29 | Final Presentation | Everyone

Ethics and Safety

Safety and Ethical Concerns
During the design and production of our balance there are a few safety considerations that we have to take into consideration. One of the safety concerns that arose is as with any electrical system making sure that we use safe and proper power equipment to make sure that we are always operating within a safe voltage. We also consider accurate measurements an important safety factor, as inaccurate measurements can lead to accidents and failures when needed for a critical system. Because of this, we will have an indicator for whether the balance has been calibrated recently. This will let the user know that either the balance has been calibrated and is accurate, or if it needs to be recalibrated.

Safety Review
Taking into consideration the safety risks we found while designing our balance, we believe that the user of the scale should have an understanding of the accuracy of the scale, from knowing when it was previously calibrated, along with an expectation of safety from the low wattage required for the operation of the scale. These factors will allow for our scale to be used in various conditions while the user can be assured they are safe.

Citations
L. S. Chao, S. Schlamminger, D. B. Newell, J. R. Pratt, F. Seifert, X. Zhang, G. Sineriz,
M. Liu, D. Haddad; A LEGO Watt balance: An apparatus to determine a mass based on the new SI. Am. J. Phys. 1 November 2015; 83 (11): 913–922. https://doi.org/10.1119/1.4929898

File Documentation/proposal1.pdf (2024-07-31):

## The Watt Balance

ECE445 Project Proposal
Justin Ansell (jansell2), Julian O’Hern (johern2), John Howard (johnlh3)
1. Introduction

Problem:

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

Solution:

Our solution for this problem involves iterating on the design created by the UIUC graduate researchers and creating a more precise and easier to use Watt Balance. We plan to improve the sensing capabilities of the device and make mechanical improvements to help support those changes. By replacing the 3d printed fulcrum of the balance with a smooth axle and bearing, we can not only reduce friction in the balance, but also use a more accurate sensor on the axle than the ultrasonic sensor the previous design used. We plan to improve the sensing of the induced current in the coil using an ammeter rather than the arduino ports as it was previously measured to further increase the accuracy of the mass calculation. We also plan to update their current MATLAB-based software implementation to a more powerful language to allow for more efficient processing of the data.

Visual Aid:

High-level requirements:

1. The device must be able to accurately measure the rotational velocity of the balance.
2. The device must be able to accurately measure the force generated by induction in the coil.
3. The device must be able to calculate the mass of the object and present it to the user in a clear and efficient manner.
2. Design
■ Block Diagram:

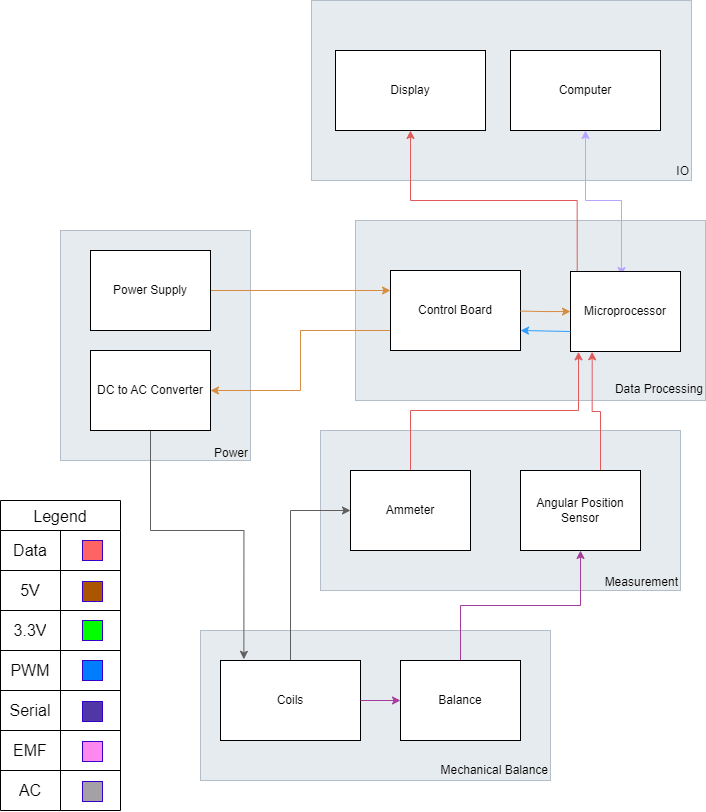
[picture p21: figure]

Device Subsystems:

Power Subsystem

Function: The power subsystem is the main source of power for all of the electronics, delivering DC power that is propagated throughout the entire device. The power subsystem also delivers a consistent and expected AC power to the coils to drive the balance force, and can be adjusted by the control board. This is important as precision in the input voltage is directly necessary to getting an accurate current reading from the ammeter.

Requirements:

Must Have | Stretch Goal

DC to AC converter to power coils

Power to the Control Board

Measurement Subsystem

Function: The measurement subsystems should both be able to measure the current induced in the coils, along with the movement and velocity of the balance as power is applied. The data from these measurements will be sent to the control board for both feedback and tuning purposes, and for calculating the mass of the object.

Requirements:

Must Have | Stretch Goal
Accurate sensing of angular position to within 5% error | Accurate sensing of angular position to within 1% error
Accurate sensing of current to within 5% error | Accurate sensing of current to within 1% error

Mechanical Subsystem

Function: The mechanical subsystem allows manipulation of the balance through the electromagnetic force generated by the coils. It also encapsulates the changes to the fulcrum of the balance to allow its angular position to be read by the angular position sensor

Requirements:

Must Have | Stretch Goal

Ability to move the balanced using the force from an induced magnetic field in the coil

Minimal interference with other electronic components (shielding if necessary)

Minimal friction in the fulcrum

Data Processing Subsystem

Function: The data processing system should be able to take in input’s from the IO, sensors, and voltage readings, and correctly allow for adjusting parameters along with calculate and output measurements.

Requirements:

Must Have | Stretch Goal

Read in measurements from position and current sensors

Convert position and current data into angular velocity and force data

Calculate the mass of the object based off the angular velocity and force data

IO Subsystem
Function: The IO subsystem will be the primary way for interacting with the control board, there will be some sort of display to give out reading from the sensors, and the mass, along with input methods to tune the inputs to the balance, such as voltage, and tune how the sensors are read.

Requirements:

Must Have | Stretch Goal

User interface to input and read data and parameters

Communication of data and parameters between a computer and the microcontroller | Setting of parameters based off automatic calibration

Display to read out the mass of the object on the balance

Tolerance Analysis:

One critical component of the device is the rotational position measurement. Looking at Hall effect sensors, which are our current frontrunners for a positional sensor, many seem to be accurate to about 0.3%. Converting the position to velocity is a derivative relationship, meaning that the error in the measurement should remain as 0.3%, which satisfies our target threshold for the velocity measurement. We also will be averaging the slope across many points to further increase the accuracy of the measurement.

3. Ethics and Safety

Our project does not have many major safety concerns. Some smaller concerns may be having fingers pinched between magnets, or risk of electrical shock from exposed coils. However, the voltages and currents involved will be relatively low, and the magnets will be fairly small, meaning that the safety risk involved is minimal. We don’t anticipate any ethical concerns arising from our project, as this is not intended to be a commercial product, and the Watt Balance is in the public domain.

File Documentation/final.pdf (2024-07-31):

# WATT BALANCE

By

Julian O’Hern
Justin Ansell
John Howard

Final Report for ECE 445, Senior Design, Spring 2024 TA: Abhisheka Sekar

1 May 2024
Project No. 76

ii

### Abstract

Our senior design project focused on the development of a Kibble balance, also known as a watt balance. This is an instrument capable of precise measurements based on electromagnetic forces and the definition of a kilogram based on fundamental constants. Our design is focused on the two main working modes of a watt balance, velocity mode in which a coil constant is calculated, and force mode in which that coil constant is used to realize some mass. We designed a custom 3D printed balance, along with a custom PCB to drive the measurements. Once assembled we found that velocity mode on our balance was inaccurate, but our force mode performed as expected. With a manual estimation of the coil constant, we were able to get accurate mass readings from our balance. The designs, failures, and successes are all documented in the following report.

iii

### Contents

iv

v

### 1. Introduction

### 1.1 Problem

Since 1879, the universal standard of a kilogram was derived from a physical mass made of a platinum-iridium alloy stored away in a vault. However, even with careful preservation in optimal conditions, over time the mass of the object drifted slightly, which is problematic for use as a constant standard. In 2019, as part of a sweeping change to the SI system, the kilogram was redefined to depend on Planck’s constant rather than the mass of a physical object as described by Boutin [2]. Researchers at the National Institute of Standards and Technology (NIST) developed a device called a watt balance (or Kibble balance, after its inventor Dr. Bryan Kibble) that uses induced magnetic fields to precisely determine the mass of a given object by measuring the rotational velocity and force generated by the balance. Following the creation of the device, NIST also released a paper [4] detailing how to make a simple version of the balance at home using LEGOs. A group of graduate researchers in the ABE department of UIUC followed this paper to make their own LEGO version of the balance, but it is imprecise in its measurements, often off by 20-30%. This is problematic for a device whose goal is to create very precise measurements.

### 1.2 Solution

Our solution for this problem involved iterating on the design created by the UIUC graduate researchers and creating a more precise and easier to use watt balance. We planned to improve the sensing capabilities of the device and make mechanical improvements to help support those changes. By replacing the 3d printed pointed fulcrum of the balance with a smooth axle and bearing, we could not only reduce friction in the balance, but also use a more accurate position sensor on the axle than the ultrasonic sensor the previous design used. We planned to improve the sensing of the induced current in the coil using a discrete current sensor rather than the Arduino ports as it was previously measured to further increase the accuracy of the mass calculation. We also planned to update their existing MATLAB-based software implementation to a more powerful language to allow for more efficient processing of the data and create an easier to use user interface to match.

### 1.3 Operation

### 1.3.1 Visual Aid

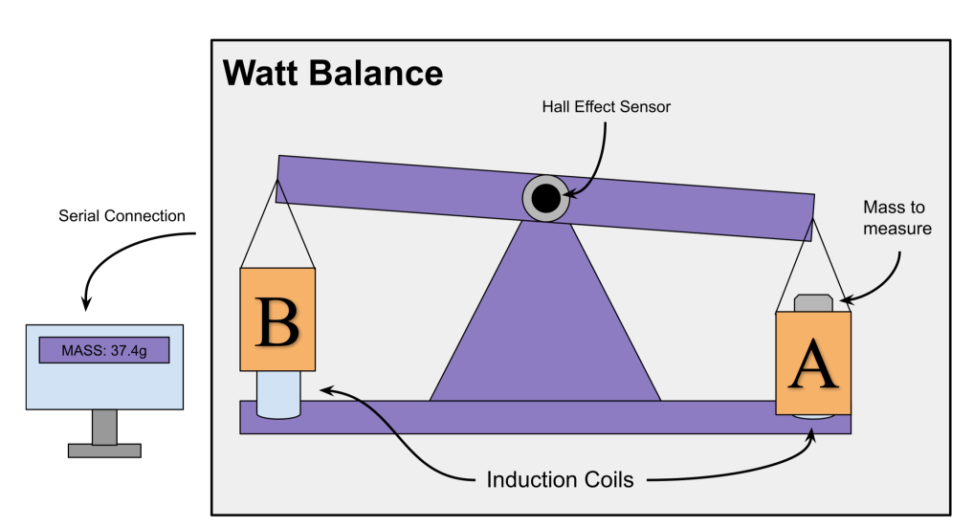
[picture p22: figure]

Figure 1: The high-level design of the balance

### 1.3.2 Velocity Mode

The first mode that the balance operates in is velocity mode. This mode is used to calculate the coil constant (also known as the flux integral) for the coil that has the mass above it, which we refer to as coil A. To achieve this, the opposite coil, coil B, is driven by a sinusoidal wave. We then measure the velocity of bucket A as it moves up and down through the coil and the voltage in coil A that is created by the induced current. Using Faraday’s laws, we can find coil A’s respective BL which we call BLvelocity as seen in Equation 1.

v(BL)velocity = V | (1)

### 1.3.3 Force Mode

The second operating mode is force mode. In force mode the balance drives coil A until it finds the current I through the coil that creates an upwards force counteracting the force of gravity, resulting in a leveled position. Then once this current is found, the mass of the object can be calculated. To do this we use the BLvelocity found in Equation 1 and the local gravitational constant to solve for the mass in Equations 2 and 3.

F = mg = I(BL)velocity | (2)

m =

I(BL)velocity g | (3)

### 1.4 High Level Requirements

### 1.4.1 Accurate Position Measurements

To meet the requirements for accurate position measurements, the device must be able to correctly measure the rotational velocity of the balance as it rotates around the fulcrum. Given that the error when using a known mass in the original ABE device was between 20-30%, we targeted <5% error for our measurements to be considered accurate, and <1% error as a stretch goal.

### 1.4.2 Accurate Force Measurements

To meet the requirements for accurate force measurements, the device must be able to correctly measure the force generated by induction in the coil as the magnet moves through it. Like the rotational velocity, we targeted <5% error for our measurements to be considered accurate, and <1% error as a stretch goal.

### 1.4.3 Communication

To meet the requirements for communication, the device must be able to communicate with the control software via a serial connection and accept input calibration parameters given by the user of the device.

### 1.5 Subsystems

### 1.5.1 Block Diagram

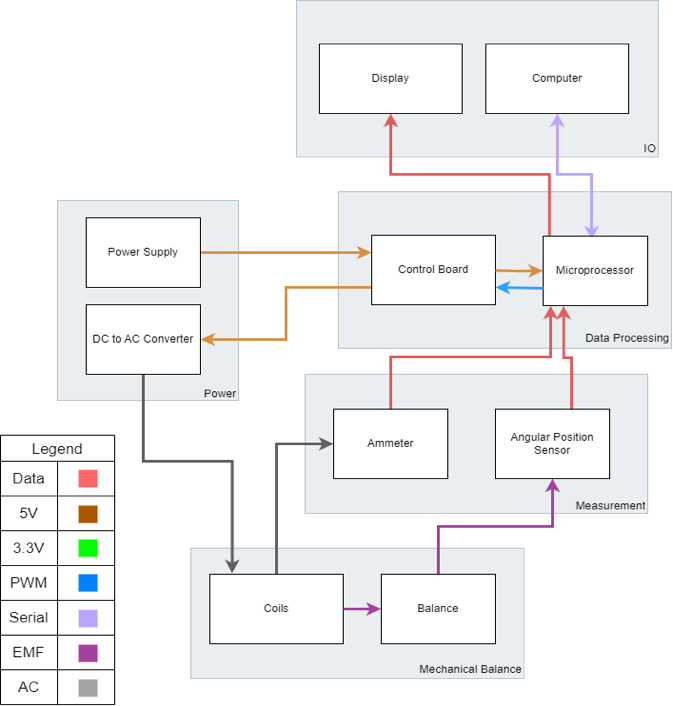
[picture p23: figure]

Figure 2: The subsystems of the balance and how they interconnect

### 1.5.2 Power Subsystem

The power subsystem plays the role of delivering the correct power and waveforms throughout the system. The primary focus of the power subsystem is to generate controllable waves to each coil. For coil B our goal was to generate a smooth bipolar sin wave between two and negative two volts with a controllable period to drive it in velocity mode. Then for coil A we needed to generate a current controlled supply. To accomplish this, we used pulse width modulation (PWM) and have a feedback mechanism that updates the duty cycle based on the current sensor.

### 1.5.3 Measurement Subsystem

The measurement subsystem encompasses all the sensors which collect the data for our calculations. It should both be able to measure the voltage induced in coil A in velocity mode and the current through coil A in force mode, along with the movement and velocity of the balance. The data from these measurements is sent to the data processing subsystem for both control feedback, tuning, and for calculating the coil constant and mass of the object.

### 1.5.4 Mechanical Subsystem

The mechanical subsystem is the physical balance itself and how it moves. It allows for the manipulation of the balance through the electromagnetic force generated by the coils. It also encapsulates the changes to the fulcrum of the balance to allow its angular position to be read by the angular position sensor.

### 1.5.5 Data Processing Subsystem

The data processing system acts as the brain for our project. The goal is it should be able to take in commands from the input output and measurement subsystems. Then with the data it should calculate and update the feedback mechanisms and send the data to the input output subsystem. The data processing subsystem should also be tunable, allowing for users to change constants to improve the performance of the balance.

### 1.5.6 Input Output Subsystem

The IO subsystem is the primary way for interacting with the balance. The goal is to have a display to read out reading from the sensors and the calculated mass and constants. It also needs to take in tuning variables to be able to change the constants, such as gravity, that are used in the data processing subsystem.

### 2 Design

### 2.2 Physical Balance

### 2.2.1 Base

There were several main design considerations that went into the base of the balance. The first was that it should be large enough to house our PCB, Hall effect sensor, and IO, as well as the associated wiring for those components. The second was that it needed to be stable enough to not move around while the arms are in motion. The third consideration was that it needed to have enough space around the fulcrum for the arms to swing without obstruction during operation. Overall, our final design for the base (Figure 3) accomplished all of these goals in a fashion that could be 3d printed easily.

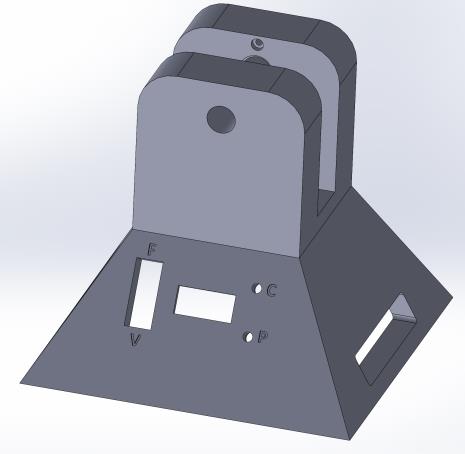
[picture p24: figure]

Figure 3: The CAD model of the base of the balance

### 2.2.2 Arms

The primary design factor on the arms of the balance was their length. They needed to be long enough to have a measurable range of motion, but short enough to be rigid and remain within the build volume of the 3d printer. Our final design for the arms (Figure 4) features a balanced length of 200mm, as well as small cutouts for the D-shaft, bearings for the buckets, as well as screw holes to attach the two halves of the arm.

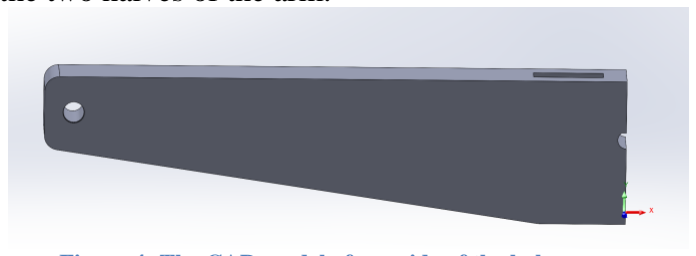
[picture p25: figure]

Figure 4: The CAD model of one side of the balance arm

### 2.2.3 Buckets

The buckets did not have as many design factors as the other parts of the balance, but considerations did have to be made for the bottom part that houses the magnets. It needed to be large enough to hold the magnets in, while being as slim as possible to avoid contacting the coils as it moved through them. Our final design of the bucket (Figure 5) features a long stalk to hold the magnets, a cup wide enough to hold different sizes of objects, as well as attachment points onto the arms.


Figure 5: The CAD model of the final bucket design

### 2.2.4 Full Assembly

The full assembly of the balance features all of the components listed above, as well as bearings to ensure smooth motion of the arms and buckets, the two coils to be driven by the device, as well as internal mounting for the PCB.


Figure 6: The completed balance assembly

### 2.3 PCB

### 2.3.1 Microcontroller

We chose to use the ATMega328PB as the microcontroller for our system. We were initially planning to use the ATMega328, as that is the one that we had practice using in class, however the PB revision contained support for two serial peripheral interface (SPI) connections, while the base 328 only has one. This would be useful to have both the SPI connection to the in-system programming (ISP) and the Hall effect sensor. We paired the ATMega with a 16 MHz crystal oscillator to allow for higher clock speeds, allowing for faster sampling of our sensors and for faster control over our voltage delivery. To connect the ADC pins on the ATMega with the coils we used a voltage shifter as pictured in Figure 7. This allowed us to read a bipolar voltage between -1.65V and 1.65V. We used one of the ADC pins for the connection to the current sensor, which delivered an analog voltage based on the read current. Two of the general pin input output (GPIO) pins we used to deliver the PWM wave to the half bridge, and another two were used to interface with an I2C connection to our DAC. Finally, we had external connectors out for both the SPI connections, and for all the additional unused GPIO pins.


Figure 7: The voltage shifter to convert 0V to 3.3V into -1.65V to 1.65V


Figure 8: The ATMega328PB microcontroller and its connections

### 2.3.2 Power Delivery

For the power delivery we needed three voltage rails. A 3.3V rail to power the microcontroller and some ICs and a 5V rail to power the rest of the ICs. We also need a -5V rail to easily be able to send a bipolar voltage signal to our coils. The 5V supply is provided to us from the USB connection, we added a 1-amp glass fuse and an electrostatic discharge protection chip, the TPD3E001DR on the 5V rail from the USB connector to protect our device. The USB to UART chip we used, the FT232RL, had a built-in voltage step down to 3.3V we could use to create our 3.3V rail. Finally, we used the ICL7660 to create the -5V rail as shown in Figure 9.


Figure 9: The ICL7660 CMOS voltage converter

### 2.3.3 Digital to Analog Converter

The digital to analog converter is a critical part of the system used for driving coil B in force mode. The MCP chip is controlled through an I2C connection to the ATMega. It is used to create a sinusoidal output between 0V and 5V. One we have our wave signal we pass it through the OP-AMP configuration seen in Figure 10. This OPA188AID shifts the wave into a range of between 1.25V and -1.25V. This can then be sent to the coil to create the sinusoidal motion.


Figure 10: The DAC and OP-AMP circuit to drive the coils

### 2.3.4 Half Bridge

The half bridge, a DRV8848, is used as the current controlled voltage output to coil A in force mode. It is controlled by the ATMega through a PWM signal. The half bridge is capable of outputting a voltage between 0 and 5V with a maximum current of 2A as specified by [3]. This is useful as when in force mode, coil A requires an ample amount of power, roughly one watt, to be able to raise the mass to a balanced position.


Figure 11: The DRV8848 H-Bridge for driving force mode

### 2.3.5 USB Connection

The USB connection to our PCB is key point in the design, as the USB both supplies the power and the communication with the host for our design. We included a 1-amp glass fuse on the power line along with an ESD protection chip on both the data and power line on the connector. The goal of this was to keep our design up with the best practices and protect our board from shorts and static discharges. We put a 5.1kΩ resistors on both CC1 and CC2, selecting to use the base power setting specified in the USB 2.0 specification seen in [5]. We routed the data lines into the FT232RL, which converts the USB signals into serial UART which we can then pass along into the UART RX and TX data lines of our ATMega. The FT232RL also has the benefit of providing a 3.3V line to use for logic ICs on the rest of our PCB. This setup allows for the optimal control of our PCB while maintaining simplicity and following the best practices to ensure safe operation.


Figure 12: The USB-C connector and UART converter for power and software input to the balance

### 2.4 Arduino Uno

### 2.4.1 New Power Delivery

Due to issues in getting our ATMega to program we had to switch to using an Arduino Uno. While this made programming much simpler it limited our ability to deliver ample power to the components. In the new design we used two of the pins to create a bipolar digital wave out to coil B for velocity mode. This was achieved by switching the between high/low and low/high on the two pins out to coil B. To drive coil A, we bit banged a PWM wave through a pin to coil A and connected the other side of coil A to ground. These methods are effective but due to the Arduino’s power limitations in the new design our current maxed out at roughly 40mA at 5V.

### 2.4.2 New Current Sensing

The Arduino had no available built in current sensor, which resulted in us calculating the current through the coil based on the voltage through the coil and the known impedance of the coil. While this measurement was sure to be less accurate, it would still allow us to operate force mode under our new circumstances.

### 2.5 Software

### 2.5.1 Control Flow

The control flow is illustrated by the flowchart in Figure 13. When the system boots, we initialize all the pins and communication interfaces. Then we enter the main loop, the first step is to read the state of the switch to understand which mode the balance is in. Then run through the respective mode operations. This cycle is continuously repeated while the balance is on.


Figure 13: The high-level control logic flowchart

### 2.5.2 Velocity Mode

In velocity mode, we make sure that coil B is the only coil being driven, then we take two position samples, and two voltage samples of coil A to update our running average of BL. This loop continues and updates the calibration LED once enough samples of BL have been taken, in our case we went with 100 samples of BL.

### 2.5.3 Force Mode

In force mode, first we ensure that coil B is not being driven. Then we look at the position of the balance. If the position is less than the balanced position then we know we need to increase the duty cycle for our PWM to coil A, meanwhile if the position is greater than the balanced position we need to decrease our duty cycle. If the balance is detected to be leveled then the current through coil A, the gravitational constant, and the calculated BL from velocity mode are used to calculate the mass. Once the mass is calculated, the system turns on the calibrated LED and displays the mass on the 4x7 segment display.

### 3. Design Verification

### 3.1 Power Subsystem

### 3.1.1 Inverter

Our goal for the inverter was to have a smooth sinusoidal output. While this was not possible due to the hardware limitations of the Arduino, we were still able to generate a bipolar square wave to drive coil B, as is visible in Figure 14. Also pictured is the power limitations of the Arduino, where each leading edge of the wave the voltage spikes to 5V then back down to roughly 3.5V. This is due to the power limitations of the Arduino Uno, which we found can supply a maximum of roughly 40mA which is more than suggested in the datasheet [1]. Given that the resistance of our coil is 84Ω it is expected that the maximum voltage would be roughly 3.36V which is what is shown in Figure 13. The solution to this would be to get a DAC that is controllable by the Arduino with a much higher maximum current, which would allow us to get both the wave form and the power we wanted. Despite this, we believe that this result was good enough to meet are expectations for this verification.


Figure 14: The square wave output from the Arduino to drive coil B

### 3.1.2 Power Supply

For the power supply to the board our verification was to make sure we were able to generate the appropriate voltages; 3.3V, 5V, and -5V. On our PCB we had probe points for each voltage rail and we found that all the required voltages were being produced. However, when we switched to use the Arduino we found that the 40mA provided by the pins were not sufficiently powerful to drive coil A in force mode, as we only had roughly one fifth the lifting power we expected. This can be seen in the PWM signal below as the Arduino pins initially try to hold 5V but the current limit means they must drop down. We believe that this verification was not adequately met in our final design.


Figure 15: The PWM signal generated by the Arduino to drive coil A in force mode

### 3.2 Measurement Subsystem

### 3.2.1 Position Sensing

The position sensing in our design was done with the Hall effect sensor fixed around the fulcrum shaft. This sensor gave us an initial trouble when programming its SPI interface. The documentation on our sensor, the ERCK 05SPI 360, was sparse, and its data sheet did not thoroughly explain its operation. We ended up needing to iterate through all possible parameters until we found some that returned the correct position data. Once we had the position data from the sensor, we could see that the sensor was very accurate with only a small amount of jitter. The accuracy of our position sensor can be seen in Figure 16, where the angle of the balance oscillates and decays in amplitude as it targets being fully balanced at a position of 0m, with a small error bound to prevent it from oscillating infinitely. We found this to be within the 5% error described in the verification and consider the position measurement to be successful.

Position (m); Current (mA); Time (ms); Force Mode

Figure 16: Position and Current over time in force mode operation

Voltage (V); Velocity (m/s); Time (ms); Mode; velocity; voltage

Figure 17: Velocity and voltage over time in velocity mode operation

### Position (m) and Current (mA) vs Time (ms) in

### Velocity (m/s) and Voltage (V) vs Time (ms) in Velocity

### 3.2.2 Voltage Sensing

Although not in our verifications, we found that verifying the ability to read the voltage caused by the induced current in coil A was pivotal in the correct operation of the balance. Figure 18 shows an example oscilloscope reading of this induced voltage waveform. While we were able to read this voltage and correlate it with the velocity as shown in Figure 18, we believe that an improved ADC with higher resolution and a higher possible sampling rate would allow us to get better results.


Figure 18: The induced current waveform in coil A during velocity mode operation

### 3.2.3 Current Sensing

In our final design, we were not able to use our current sensor due to using the Arduino instead of the PCB. Because of this, we had to estimate the current through coil A. We could do this reasonably as we knew that the pin would always supply 40mA of current when set high, and the duty cycle for the PWM corresponded the percentage of time the pin was high, using equation 4, we were able to get an accurate estimation of the current. While we don’t believe that this satisfied our verification as it’s only an estimate and therefore could is at times inaccurate with fluctuations in the supply current from the Arduino, it worked well enough to be able to accurately read a mass in force mode.

current = duty_cycle ∗ 40mA | (4)

### 3.3 Mechanical Subsystem

### 3.3.1 Movement from Coil

We were able to verify that the coils moved properly simply by running the balance in velocity mode, in which the arms of the balance oscillated up and down as expected. We did have a small issue with the buckets on the ends of the arms bottoming out and bumping into the coils at the bottom of their arc, but we do not believe this caused any major issues with the operation of the device.

### 3.3.2 Electromagnetic Interference

We did not have a Gaussmeter in the lab to verify there was no electromagnetic interference, and such a device was outside the budgetary range of this project, but driving the coils at full strength did not lead to any change in the measurements from the Hall effect sensor (the most electromagnetically sensitive component), so we can be reasonably confident that there is no significant interference between the coils and any other electrical component within the project.

### 3.3.3 Friction

Due to the current restrictions through the Arduino, the 10-gram test mass we had planned to be among the smallest measurable values was beyond the lifting capabilities of the coils. However, in the force mode tests with varying masses, we were able to see distinct and uniform measurements from changes in mass of less than a third of a gram, which is an indicator that friction in the bearings is even less of a concern than we originally thought.

### 3.4 Data Processing Subsystem

### 3.4.1 Receiving Measurements

For the data processing subsystem, it was important that we were able to interface with all of our sensors and receive data into the program. We initially found an issue when we were connecting our Hall effect sensor, as the documentation did not thoroughly lay out the parameters for connecting it through SPI. The special SPI interface worked by combining the MISO and MOSI lines into a single data line, this was done by bridging the two with a 10kΩ resistor. Once this was completed, we ran a suite of tests trying different clock speeds, delays between packets, and SPI modes until we found a combination that reliably delivered us accurate and consistent results. To receive measurements from the analog pins on the Arduino we just had to make sure that the coils were connected and that the pin modes were set to input. We are then easily able to read the voltages and use them in software, which meets the requirement to get measurements into our data processing subsystem.

### 3.4.2 Intermediate Calculations

The main intermediate calculation was to find the value of the flux integral, which is our coil constant. This is the value we get as a result of Equation 1 where we divide the voltage by the velocity. To so the accuracy of our calculation we can plot voltage against velocity in velocity mode and it should give a straight line with a slope of BL. However, as pictured in Figure 18, our data is highly nonlinear, which leads to poor accuracy in the BL calculation. This, combined with the jitteriness of our estimated current measurements due to the lack of a dedicated current sensor, leads to inaccurate final mass calculations. For the data processing system, we found it was easier to keep a running average to estimate BL. Figure 19 illustrates the inaccuracy of this running average, and that the average is raised by the high amount of error and noise in the voltage and velocity measurements. While this subsystem is successful at calculating an intermediate value as described in the verification it follows the adage of garbage in, garbage out as our data contains no clear way of finding an accurate BL.

Voltage (V); Velocity (m/s); Voltage (V) vs Velocity (m/s)

Figure 19: Voltage vs velocity in velocity mode operation, note that the slope should equal BL

Time (ms); BL (T*m) vs Time (ms) in Velocity Mode; Mean BL

Figure 20: BL and Mean BL over time in velocity mode

### 3.4.3 Mass Calculations

For calculating the mass of the object in the bucket we use Equation 3. With the BL we collected in force mode we can use our current estimation, along with the gravitational constant to figure out the mass of the object. As seen in Figure 21 were successfully able to calculate masses up to roughly 4.5 grams although we were off by a linear factor. As we know our BL is highly inaccurate, this makes sense, given that the BL term in the formula is linear. Our mass measurement does increase linearly with an increase in mass, with little error. This shows that with a more accurate velocity mode and BL calculation our mass measurements would be correct. We believe that our mass calculations successfully demonstrate the balance’s ability and pass the verification.

Mass (g); Number of Nuts Weighed; Measured Mass; True Mass

Figure 21: Incrementally adding mass and comparing measured vs known mass

### 3.5 Input Output Subsystem

### 3.5.1 User Interface Software

The goal for the user interface software was to verify user input of parameters and run the measurement program once using the control program. Before we switched to the Arduino, we had a small python program written to communicate through serial with the PCB. Once we switched to the Arduino, we found it was easier to use the built in Arduino serial library along with updating the parameters in the sketch. We had a section of definitions for the tuning parameters, this included gravity, the current feedback constant, and the zero position of the balance. The balance also prints out through serial over the USB the readings of every active sensor depending on the mode. We believe that the verbosity and the ease of use of the Arduino software help us pass this verification.

### 3.5.2 Front Display

Our front display was relatively simplistic, containing a switch to alternate between force and velocity modes, an indicator LED for power status, a second indicator LED for calibration status, and a digital readout to display the calculated mass once it has been calculated. It was integrated directly into the base of the balance for ease of use and proximity to the PCB housed within.


Figure 22: The front display of the balance

1 | 2 | 3 | 4 | 5 | 6 | 7 | 8 | 9 | 10 11 12 13 14 15 16 17

### Mass (g) vs Number of 0.318g Hex Nuts Weighed

### 4. Costs

### 4.1 Parts

Physical Part | Unit Cost | Quantity | Subtotal Cost
Arduino Uno | $27.60 | 1 | $27.60
ERCK 05SPI 360 | $43.00 | 1 | $43.00
Current Sensor | $1.57 | 1 | $1.57
LED Screen | $3.50 | 1 | $3.50
PLA filament | $20.00 | 1 | $20.00
Copper Magnet Wire | $9.99 | 2 | $19.98
Bearings | $0.91 | 2 | $1.82
TRYMAG Small Strong Magnets | $15.99 | 1 | $15.99
D-Shaft | $1.67 | 1 | $1.67
ATMEGA328PB-AU | $1.47 | 1 | $1.47
MCP2200-I/SO | $2.35 | 1 | $2.35
ACS70331EOLCTR-2P5U3TR-ND | $2.71 | 1 | $2.71
USB4085-GF-A | $0.85 | 1 | $0.85
LED 4x7 Segment Display (Pack of 6) | $8.71 | 1 | $8.71
ACS70331EOLCTR-2P5B3 | $3.00 | 1 | $3.00
DRV8848PWP | $2.95 | 1 | $2.95
ICL7660CBAZ-T | $2.03 | 1 | $2.03
OPA188AIDBVT | $2.86 | 1 | $2.86
TPD3E001DRLR | $0.52 | 1 | $0.52
FT232RNL | $4.80 | 1 | $4.80
IA0505S | $5.82 | 1 | $5.82

### 4.2 Labor

Labor Type | Number of Workers | Hourly Cost | Total Hours | Subtotal Cost
ECE Students | 3 | $50 | 4hr* x 15 weeks | $9,000

### 4.3 Total

The total cost of our project including parts and labor was $9173.20.

### 5. Conclusion

### 5.1 Accomplishments

There are many areas of the project in which we are quite proud of our accomplishments. The first such area is our PCB design. Our group members had no prior experience designing a PCB from scratch, and only limited experience populating and soldering premade PCBs in other contexts. With only a few weeks of learning and testing, we were able to design and populate multiple revisions of our PCB, and despite a few small oversights and issues with the bootloader, we were able to make a final design that we were happy with. We were also particularly enthusiastic about the performance of the Hall effect sensor and force mode overall, since it was able to provide very good results and linearity, even with its limited range of test masses.

### 5.2 Uncertainties

Although we were overall happy with the output and results of our project, there are still several areas in which we could have improved throughout the process. One such area is doing more quantitative analysis about the currents and voltages required for operation during the design phase, which would better inform our component and coil choices. Another area we felt lacked a little bit was rigorous testing and simulation of the PCB, as both major iterations of the PCB design had small issues, such as missing grounding pins or components having the wrong footprints. Catching these issues before we sent the board designs out for production would have helped our workflow a lot and limited the number of modifications we had to do later in the assembly process. Additionally, picking a more commonly used Hall effect sensor would have saved a lot of development time trying to guess at settings based on limited information available in the documentation. Lastly, starting on the code earlier in the development process would have allowed us to catch some of the sensor issues earlier, as well as give us more time to tune the different parameters.

### 5.3 Ethical considerations

We had a few safety and ethical considerations that we had to take into consideration while designing this device. One of the safety concerns that arose is as with any electrical system making sure that we use safe and proper power equipment to make sure that we are always operating within a safe voltage. We also consider accurate measurements an important safety factor, as inaccurate measurements can lead to accidents and failures when needed for a critical system. Because of this, we designed the balance to have an indicator for whether the balance has been calibrated and is ready to measure. This lets the user know that either the balance is accurate or not, improving the reliability and safety of the instrument.

### 5.4 Future work

While we feel comfortable with the amount of features we chose to tackle with this project, there are many other potential inclusions that could be incorporated into a future version. The simplest of these features would be a dedicated power button, as our device can only be powered off by unplugging it. Another such improvement would be designing a more compact PCB, through minimizing gaps as well as hardware choices, which would allow our printed base to be smaller as well. Additionally, one of the uses for the original NIST watt balance was to determine a precise value for Planck’s constant, which our device should be able to do with a few software changes, using the difference between unit definitions across the two modes. Next, we would include a more robust balanced level detection sensor, rather than relying on the zero position of the Hall effect sensor, to be more precise with our measurements. Another change that would have allowed us to skip many of the issues we encountered with programming our PCB would be to pre-flash the bootloader onto the microcontroller before soldering it on, then program it directly through the USB-C port, eliminating the need for the ISP programmer connection. Additionally, we could have more detailed feedback from the device using a full LCD screen that would be able to show the calculated values for the coil constants, as well as display sensor information that could previously only be read through an oscilloscope or a debugging program. Lastly, there are still plenty of improvements to be made to the physical design, removing the bottoming out issue with the buckets, and having a more robust mounting system for the coils.

### 5.5 Acknowledgements

We would like to thank the researchers in the Agricultural and Biological Engineering for pitching the project and guiding us through their work.

### References

[1] Arduino Uno Rev3 SMD, datasheet, Arduino, Accessed April 2024. [Online], Available: https://media.digikey.com/pdf/Data%20Sheets/Arduino%20PDFs/A000073_Web.pdf
[2] C. Boutin, “NIST's Newest Watt Balance Brings World One Step Closer to New Kilogram” June 2016. [Online], Available: https://www.nist.gov/news-events/news/2016/06/nists-newest-watt-balance-brings-world-one-step-closer-new-kilogram (https://www.nist.gov/news-events/news/2016/06/nists-newest-watt-balance-brings-world-one-step-closer-new-kilogram)
[3] DRV8848 Dual H-Bridge Motor Driver, datasheet, Texas Instruments, Oct. 2014. [Online], Available: https://www.ti.com/lit/ds/symlink/drv8848.pdf
[4] L. S. Chao, S. Schlamminger, D. B. Newell, J. R. Pratt, F. Seifert, X. Zhang, G. Sineriz,
M. Liu, D. Haddad, “A LEGO Watt balance: An apparatus to determine a mass based on the new SI,” Am. J. Phys., Nov. 2015. [Online], Available: https://doi.org/10.1119/1.4929898
[5] Universal Serial Bus 3.0 Specification, Rev 1.0, Nov. 2008. [Online], Available: https://www.maxrev.de/files/2014/08/usb_3_0_english.pdf

### Appendix A Requirement and Verification Tables

### Power Subsystem

Requirement | Verification
DC to AC converter (inverter) to the power coils. | Use an oscilloscope on the waveform sent to the coils to make sure they are consistent, and the desired waveform.
5v to the control board from the power supply. | Probe the voltage out of the power supply to make sure the voltage is correct and will not damage the components.

### Measurement Subsystem

Requirement | Verification
Accurate sensing of angular position to within 5% error. | Begin with the balance at 0 degrees, then place a heavy object in the measurement area to ensure that it rotates as far as it can go. Compare the difference between the two measured values of the position sensor to the known maximum travel distance and see whether it is within 5% error.
Accurate sensing of current to within 5% error. | To verify, place the leads of an oscilloscope across the current sensor, then run the measurement program. Measure the current using the oscilloscope and make sure it matches with the measured value to within 5% error.

### Mechanical Subsystem

Requirement | Verification
Ability to move the balance using the force from an induced magnetic field in the coil | To verify, apply varying currents to one coil, and observe whether the balance moves as a result. Repeat with the other coil to make sure both coils are capable of moving the balance.
Minimal interference with other electronic components (shielding if necessary) | To verify, use a gaussmeter to measure the emf at the coils and an ammeter to measure the induced current. When each electrical system is activated (apart from the inverter) measure the EMF and the induced current to be sure that no interference exists.
The device must have minimal friction in the pivot such that a 10 | To verify, place a known 10 gram object on the measurement side of the balance. Then, run the force and velocity measurements on the balance using the control

gram weight is measurable to within the 5% accuracy tolerance.

software and see if the calculated mass value displayed is within 5% of the known mass.

### Data Processing Subsystem

Requirement | Verification
Read in measurements from position and current sensors | To verify, run the measurement program and check that the measurements from both the position and current sensors are displayed in the control program.
Convert position and current data into angular velocity and force data | To verify, run the measurement program and check that the calculated values displayed in the control program match up with those calculated by hand given the measurements from the sensors.
Calculate the mass of the object based off the angular velocity and force data | To verify, run the measurement program and check that the calculated mass displayed in the control program matches with the value calculated by hand given the measurements from the sensors.

### IO Subsystem

Requirement | Verification
User interface software to input control parameters for the balance | To verify user input of parameters, run the measurement program once using the control program. Then, edit the configuration values in the control program. Finally, run the measurement program again and see if the resulting measurements have changed from their original values based on the new tuning parameters.
Display to read out the mass of the object on the balance | To verify the display of data, run the measurement program using the control program, then check both the control software and the LED screen to confirm that they both display the same measured mass
Appendix B | Schedule
Week | Goals | Team Members
2/19 | Fix and submit Proposal for Regrade Complete and Submit Design Document | Everyone Everyone
2/26 | Design Review | Everyone

| Make revisions to design document Design PCB PCB Review | Everyone Everyone Everyone
3/4 | Teamwork Evaluation PCB revisions | Individual Everyone
3/11 | Spring Break
3/18 | Start to design software to work with new PCB and sensors Start to construct and iterate designs of balance | Julian John, Justin
3/25 | Test to make sure balance fits within expected tolerances Revisions to Software Revisions to Balance | John, Justin Julian John, Justin
4/1 | Make sure the balance and software interact correctly Revisions to Software Revisions to Balance | Everyone Julian John, Justin
4/8 | Small refinements and tuning to the final version of the balance. Make sure software is stable and accurate. | John, Justin Julian
4/15 | Mock Demo | Everyone
4/22 | Final Demo Mock Presentation | Everyone Everyone
4/29 | Final Presentation | Everyone

### Appendix C PCB Schematic


### Appendix D PCB Layout


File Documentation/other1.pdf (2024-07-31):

# Watt Balance

# Electrical & Computer Engineering

# Team 76 Justin Ansell, Julian O'Hern, John Howard

# A p r i l 2 9 , 2 0 2 4


# The Watt Balance

## The Watt balance, also known as a Kibble balance was invented by Dr. Bryan Kibble. It is an instrument that finds the

mass of an object through electromagnetic force and gravity. Additionally, it can be used to measure Planck’s constant.

# Our Balance

## Our goal was to replicate one of these balances in a cost

effective and accurate manner.

G R A I N G E R E N G I N E E R I N G

# Introduction

E L E C T R I C A L & C O M P U T E R E N G I N E E R I N G

The NIST-4 Kibble Balance [1]

# A LEGO® Balance

## Researchers at the National Institute of Standards and Technology (NIST) wrote a paper detailing the process of

how to create a DIY LEGO Watt balance.

# A Second Balance

## A group of graduate students from the UIUC ABE department used the NIST paper to create their own version of the LEGO Watt balance. They pitched a project to create a more

refined version.

# Background


The NIST LEGO® Watt Balance [2]


The UIUC ABE Graduate LEGO® Watt Balance

# Balance Operation Modes

# Velocity Mode

## Drives coil B and measures the velocity of the basket and the

induced voltage in coil A.

# Force Mode

## Drives coil A and measures the current required to cancel out

the gravitational force.

## Combining the Results

## In velocity mode: V = BLv

## In force mode: F = BLI = mg

## Solving for mass: m =

VI
gv

# How it Works


Velocity Mode | Force Mode

# Design Goals

## Improve upon the accuracy of the ABE graduate team’s

LEGO® version.

# Hall Effect Potentiometer

## The ABE team used an ultrasonic sensor, which we changed

for a Hall effect potentiometer.

# Mechanical Improvements

## Our balance is fully 3d printed and uses a bearing around an

axle as the fulcrum.

# Design Goals


Our Final Balance Design


E L E C T R I C A L & C O M P U T E R E N G I N E E R I N G | G R A I N G E R E N G I N E E R I N G

# Block Diagram


# First PCB Iteration

## Our first PCB had circuitry for our ATmega microcontroller, connections to a current sensor, pins outs to the Hall

effect sensor, and a USB-C port.

# PCB Design Changes


# Updated PCB Schematic

E L E C T R I C A L & C O M P U T E R E N G I N E E R I N G | G R A I N G E R E N G I N E E R I N G

# New Power Components


# More Power Circuitry

## Added an H-Bridge, DAC, OP-AMP, and a

Voltage Converter.


# The First PCB

## The first iteration of the PCB layout used placeholder footprints for the Hall effect sensor and

voltage measurements.

# Mistakes

The footprint for the crystal oscillators was wrong,

## and a few components were on the back of the

board.

# PCB Layout V1

# PCB Layout V2


# Way bigger

## The old PCB was 75x50mm, V2

ended up being 120x95mm.

# Changed Footprints

Updated footprint for the oscillator,

## switched the Hall effect footprint to match the ISP footprint, changed

voltage I/O to use Molex connectors.

# New Mistakes

## Grounding was missing on H-Bridge and USB-UART, OP-AMP Footprint

was wrong.

# Switch to Arduino


Problems getting the ATMega to program forced a change in hardware.

# Software


# The Differences

# Original ATMega Software

Lots of HAL.

Custom Serial Program.

# New Arduino Software

Followed same general design.

More high level.

Helpful Libraries.

# Power Subsystem

# Power Subsystem Requirements

DC to AC converter to the power coils.

5 volts to the control board from the power supply.

# Coil B (Bipolar Wave) – Velocity Mode

# Velocity Mode – Power Subsystem

# Coil A (Induced) – Velocity Mode

# Force Mode – Power Subsystem


# Coil A (PWM) – Force Mode

# Mechanical Subsystem

# Mechanical Subsystem Requirements

The ability to move the magnets from the current driving the coil.

Minimal interference between electrical components.

# Minimal friction in the pivot, such that the device can measure 10 grams within 5%

accuracy.


# Movement of balance from Coil A in force mode

# Mechanical Subsystem

# Measurement and Data Processing Subsystems

# Measurement Subsystem Requirements

# Accurate sensing of position to within 5%

error.

# Accurate sensing of current to within 5%

error.

# Data Processing Subsystem Requirements

# The ability to read in measurements from the

position and current sensors.

# Convert position and current data into

velocities and forces.

# Calculate the mass of an object based on the

data.

# Velocity Mode Demonstration


# CHART / GRAPH

# (Short commentary or relevant information about the contents of the chart/graph.)

# Velocity Mode Operation – Measurement Subsystem

## Velocity (m/s) and Voltage (V) vs Time (ms) in Velocity Mode

Voltage (V); Velocity (m/s); Time (ms)

# Velocity Mode Inaccuracy – Measurement Subsystem

## Voltage (V) vs Velocity (m/s)

Voltage (V); Velocity (m/s)

Measured Average BL = 0.0665 T * m

# BL Calculation in Velocity Mode – Data Processing Subsystem

## BL (T*m) vs Time (ms) in Velocity Mode

Time (ms); Average BL (T*m)

# Force Mode Operation – Measurement Subsystem

## Position (m) and Current (mA) vs Time (ms) in Force Mode

Position (m); Current (mA); Time (ms)

# Mass Calculation In Force Mode – Data Processing Subsystem

## Mass (g) vs Number of 0.318g Hex Nuts Weighed

Mass (g); Measured Mass; True Mass

Number of Nuts Weighed

# IO Subsystem

# IO Subsystem Requirements

Software that allows for the user to input control parameters into the balance.

Display to read out the mass and the state of the balance.

# IO Subsystem

# Computer Parameter Control

# Front IO


# What We Learned

Making a schematic and picking parts.

PCB design.

Designing for accuracy.

# What to do Differently

More quantitative analysis.

More thorough PCB testing / simulation.

## Develop code early

# Conclusions

# Areas for Improvement

# Hall Effect Sensor

# Power Button

# Physical Design

# Ease of Programming

# Improved IO Feedback

# Balanced Level Detection

# Measuring Planck's Constant

# More Condensed PCB

# Future Improvements

[1] Kilogram: The Kibble Balance. NIST. 2 June 2021. https://www.nist.gov/si-redefinition/kilogram-kibble-

## balance (https://www.nist.gov/si-redefinition/kilogram-kibble-balance)

[2] L. S. Chao, S. Schlamminger, D. B. Newell, J. R. Pratt, F. Seifert, X. Zhang, G. Sineriz, M. Liu, D. Haddad; A LEGO Watt balance: An apparatus to determine a mass based on the new SI. Am. J. Phys. 1 November 2015;

## 83 (11): 913–922. https://doi.org/10.1119/1.4929898

# Citations

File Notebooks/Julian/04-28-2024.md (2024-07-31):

# Final testing

- Balance works, verifying with oscilloscope
- took pictures and videos for presentation





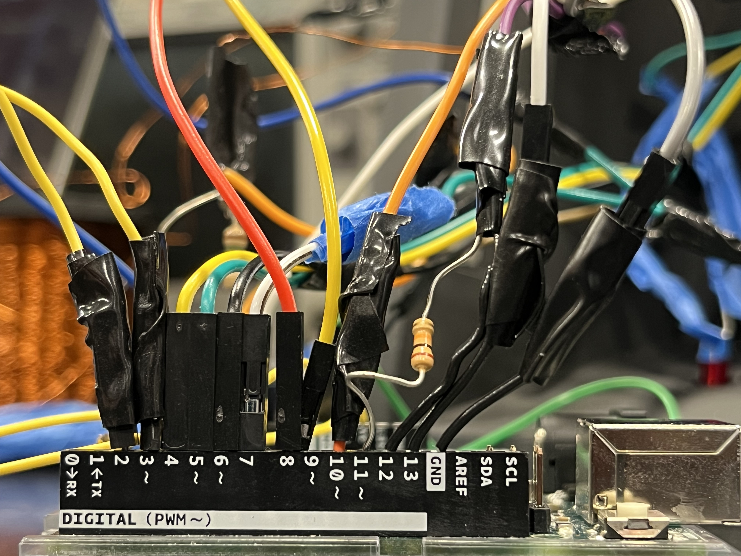
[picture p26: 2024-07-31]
Documentation/other2.jpeg

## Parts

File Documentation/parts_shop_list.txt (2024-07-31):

2x MBR0520 Diodes
1x 5mm Green LED  
1x 5mm Blue LED
1x 5mm Red LED
1x 5mm White LED
6x 1N5819 Diode
1x 1A Resettable Fuse LVR100
1x 16mhz crystal
1x Switch
1x 330 ohm Resistor
3x 470 ohm Resistors
2x 4k Resistors
1x 6k Resistor
14x 1x2 Molex Male
1x 2x3 Molex Male

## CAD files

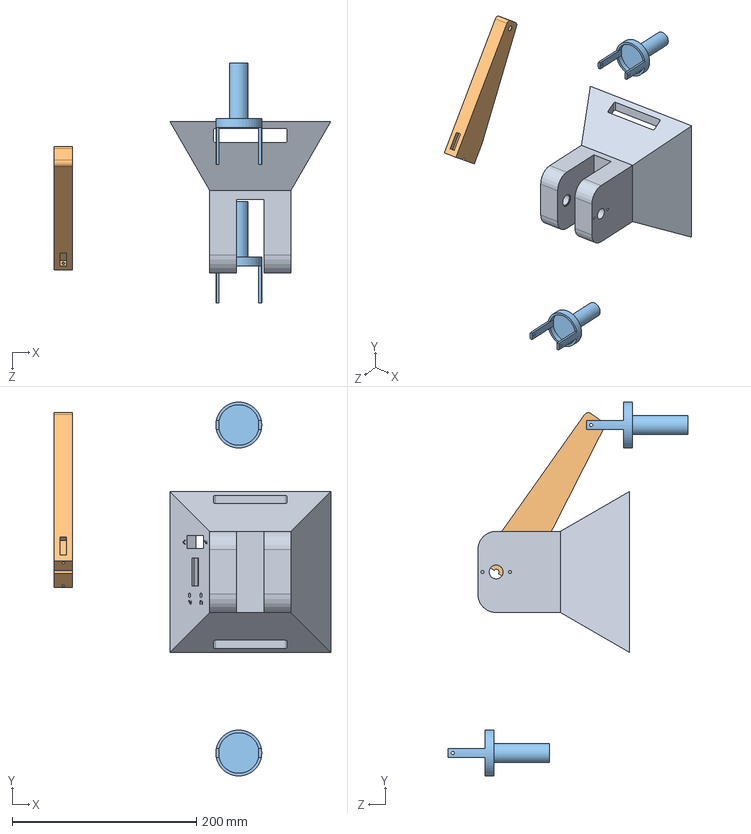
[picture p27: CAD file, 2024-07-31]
Balance CAD Files/BalanceAssm.SLDASM
300.6 x 406.4 x 260.4 mm
BalanceBase
BalanceArm
BalanceBasket x 2

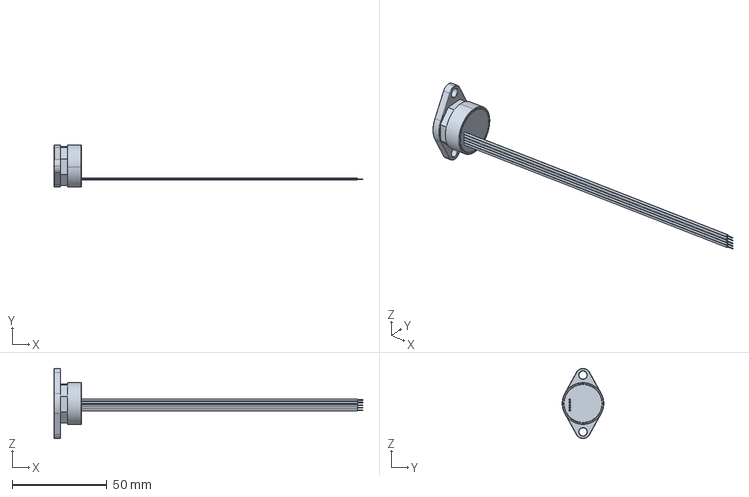
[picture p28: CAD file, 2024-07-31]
Balance CAD Files/HallEffectSensor.stp
163.1 x 22.0 x 37.0 mm

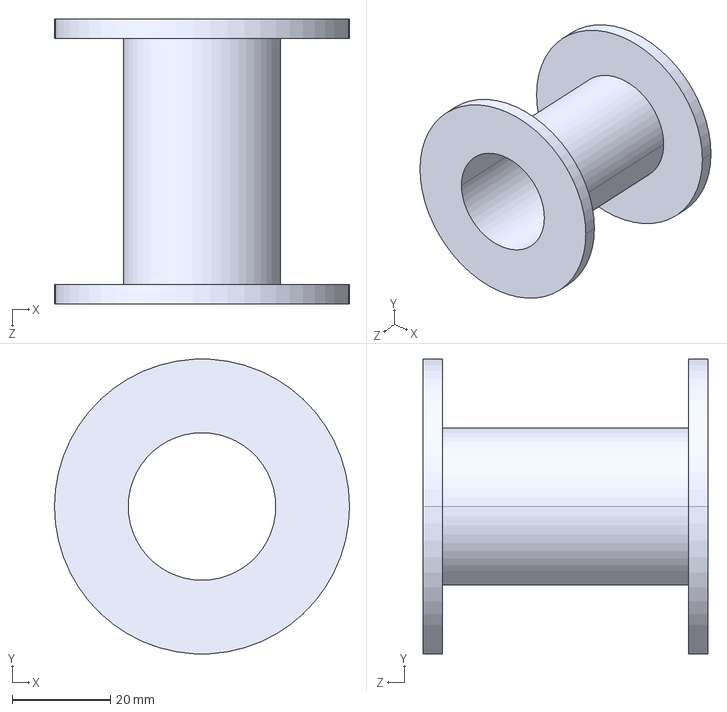
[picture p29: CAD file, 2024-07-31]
Balance CAD Files/STEP Files/CoilSpool.STEP
60.0 x 59.9 x 58.0 mm

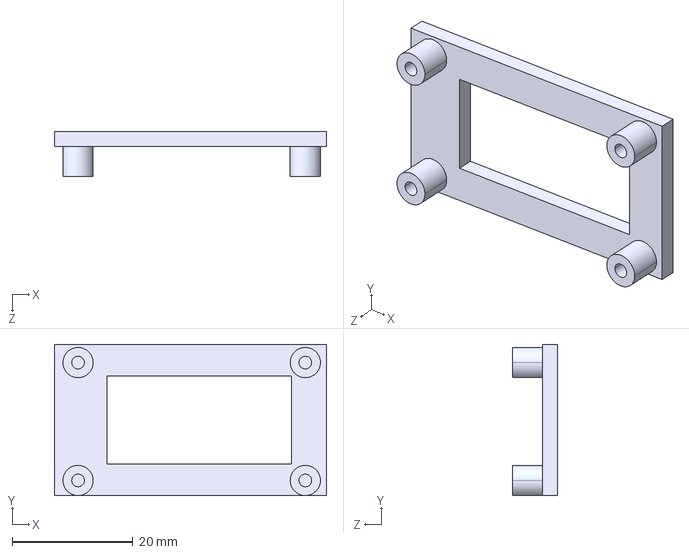
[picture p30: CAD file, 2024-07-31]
Balance CAD Files/STEP Files/Test7SegmentFaceplate.STEP
45.0 x 25.0 x 7.50 mm

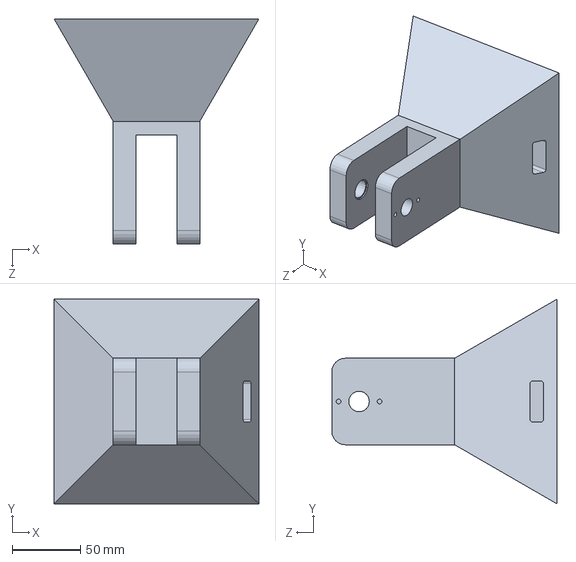
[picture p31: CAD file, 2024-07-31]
Balance CAD Files/BalanceBaseOriginal.SLDPRT
150.0 x 150.0 x 165.0 mm

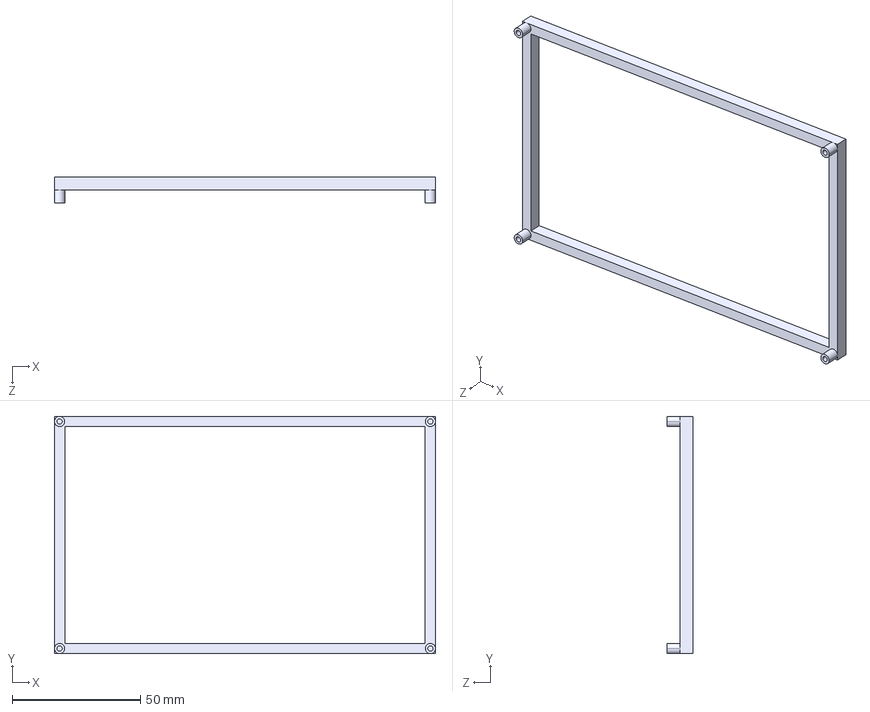
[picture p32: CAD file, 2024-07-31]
Balance CAD Files/STEP Files/TestBoardMount.STEP
148.5 x 92.5 x 10.0 mm

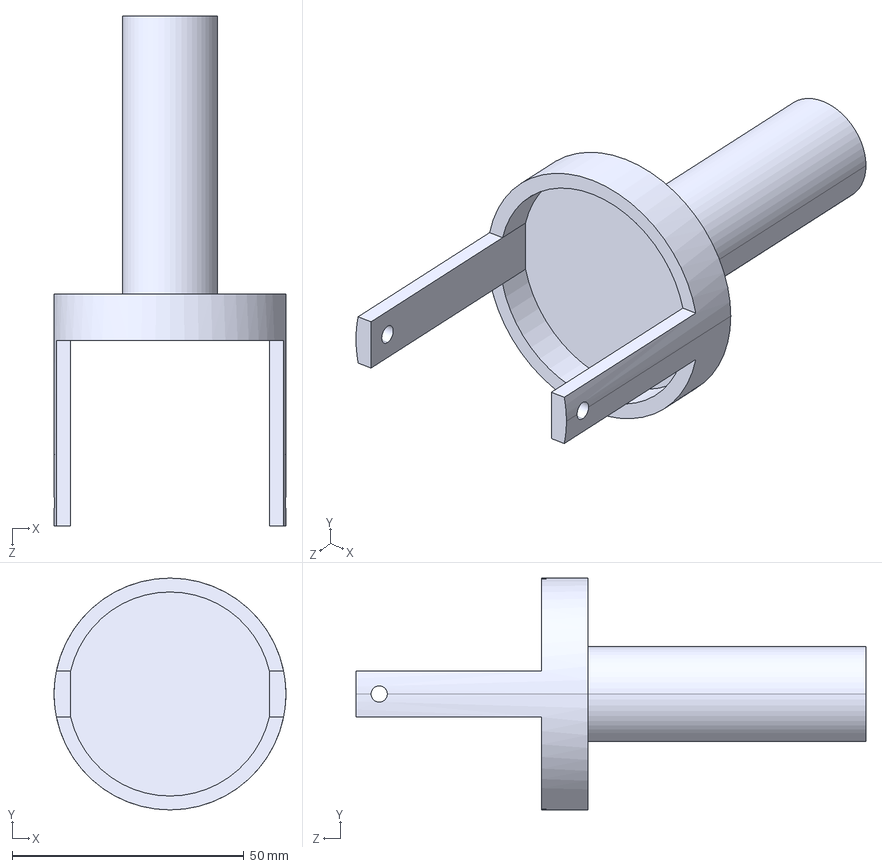
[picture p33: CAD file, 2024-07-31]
Balance CAD Files/STEP Files/BalanceBasket.STEP
50.0 x 50.0 x 110.0 mm

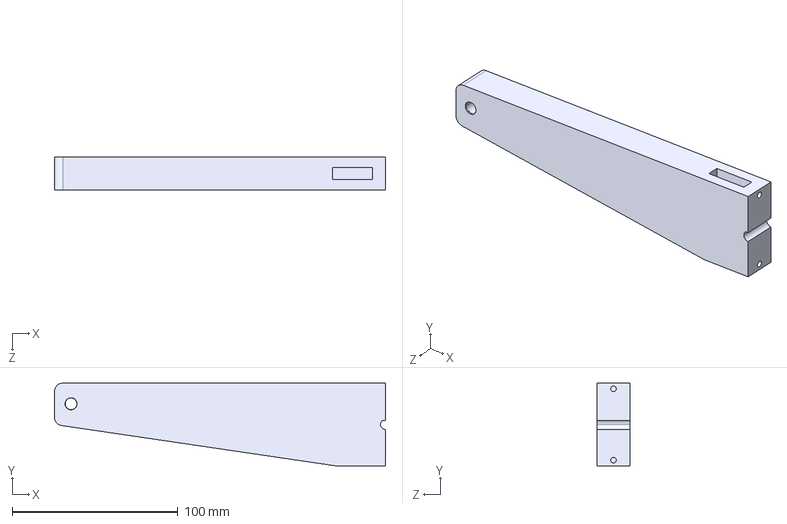
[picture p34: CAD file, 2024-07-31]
Balance CAD Files/STEP Files/BalanceArm.STEP
200.0 x 50.0 x 20.0 mm

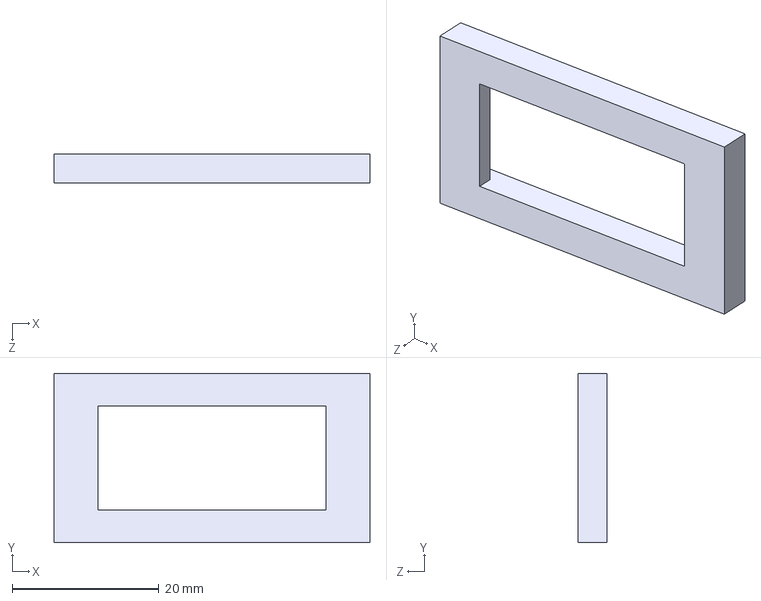
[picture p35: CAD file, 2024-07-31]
Balance CAD Files/STEP Files/TestSwitchMount.STEP
43.0 x 23.0 x 4.00 mm

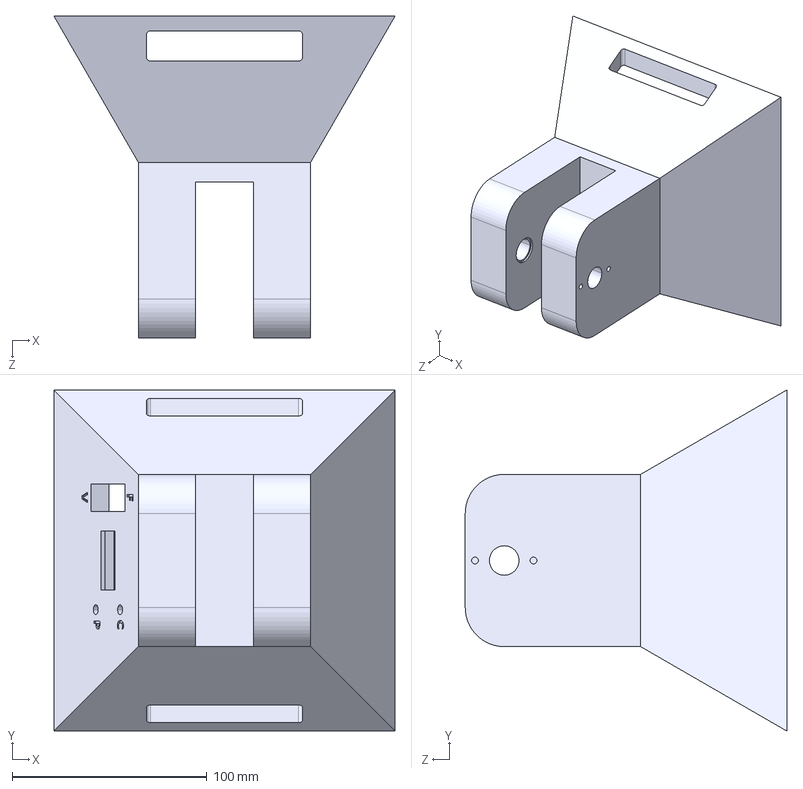
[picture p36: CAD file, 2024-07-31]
Balance CAD Files/STEP Files/BalanceBase.STEP
175.0 x 175.0 x 165.0 mm

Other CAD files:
Balance CAD Files/BalanceArm.SLDPRT
Balance CAD Files/BalanceBase.SLDPRT
Balance CAD Files/BalanceBasket.SLDPRT
Balance CAD Files/CoilSpool.SLDPRT
Balance CAD Files/HallEffectSensor.SLDPRT
Balance CAD Files/Test7SegmentFaceplate.SLDPRT
Balance CAD Files/TestBoardMount.SLDPRT
Balance CAD Files/TestSwitchMount.SLDPRT

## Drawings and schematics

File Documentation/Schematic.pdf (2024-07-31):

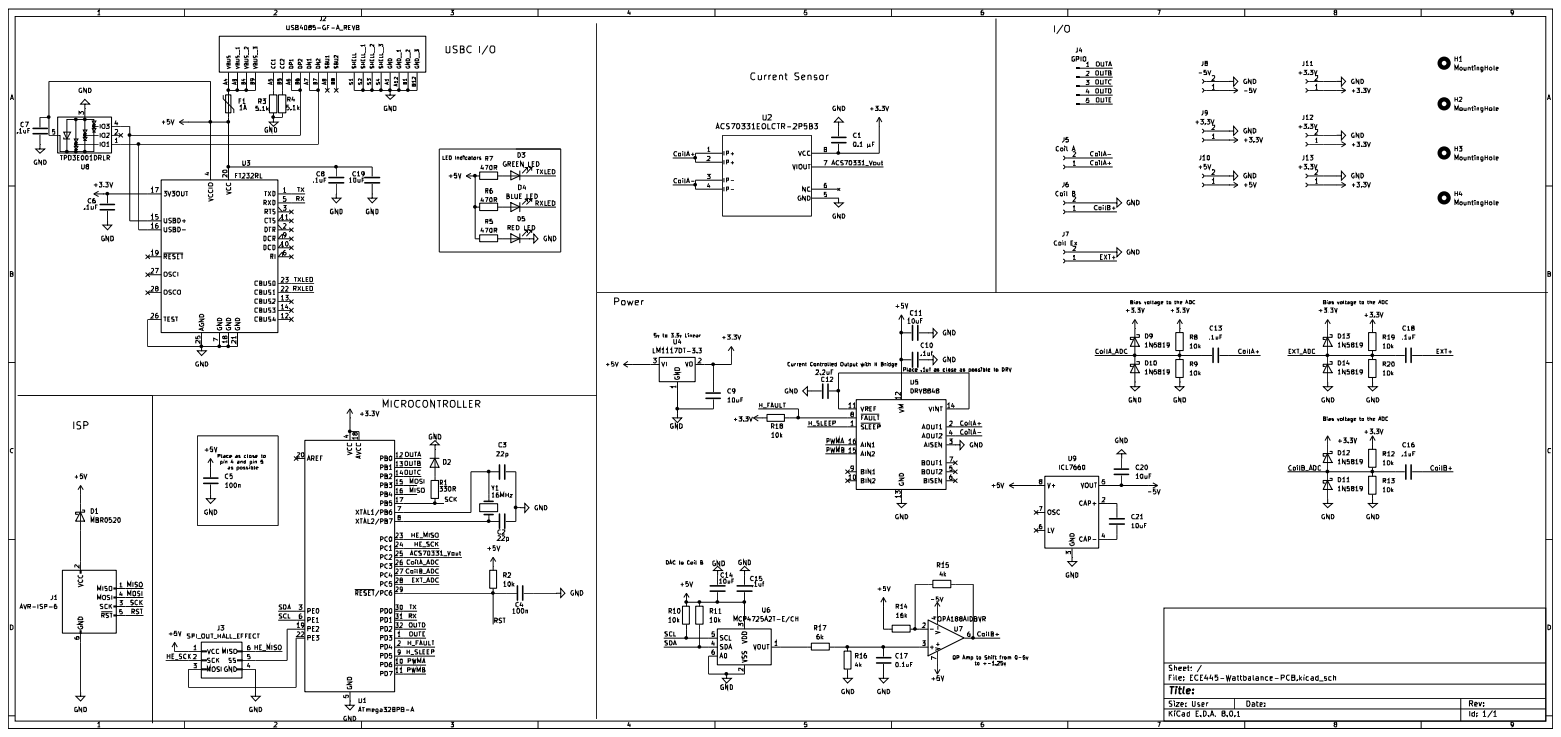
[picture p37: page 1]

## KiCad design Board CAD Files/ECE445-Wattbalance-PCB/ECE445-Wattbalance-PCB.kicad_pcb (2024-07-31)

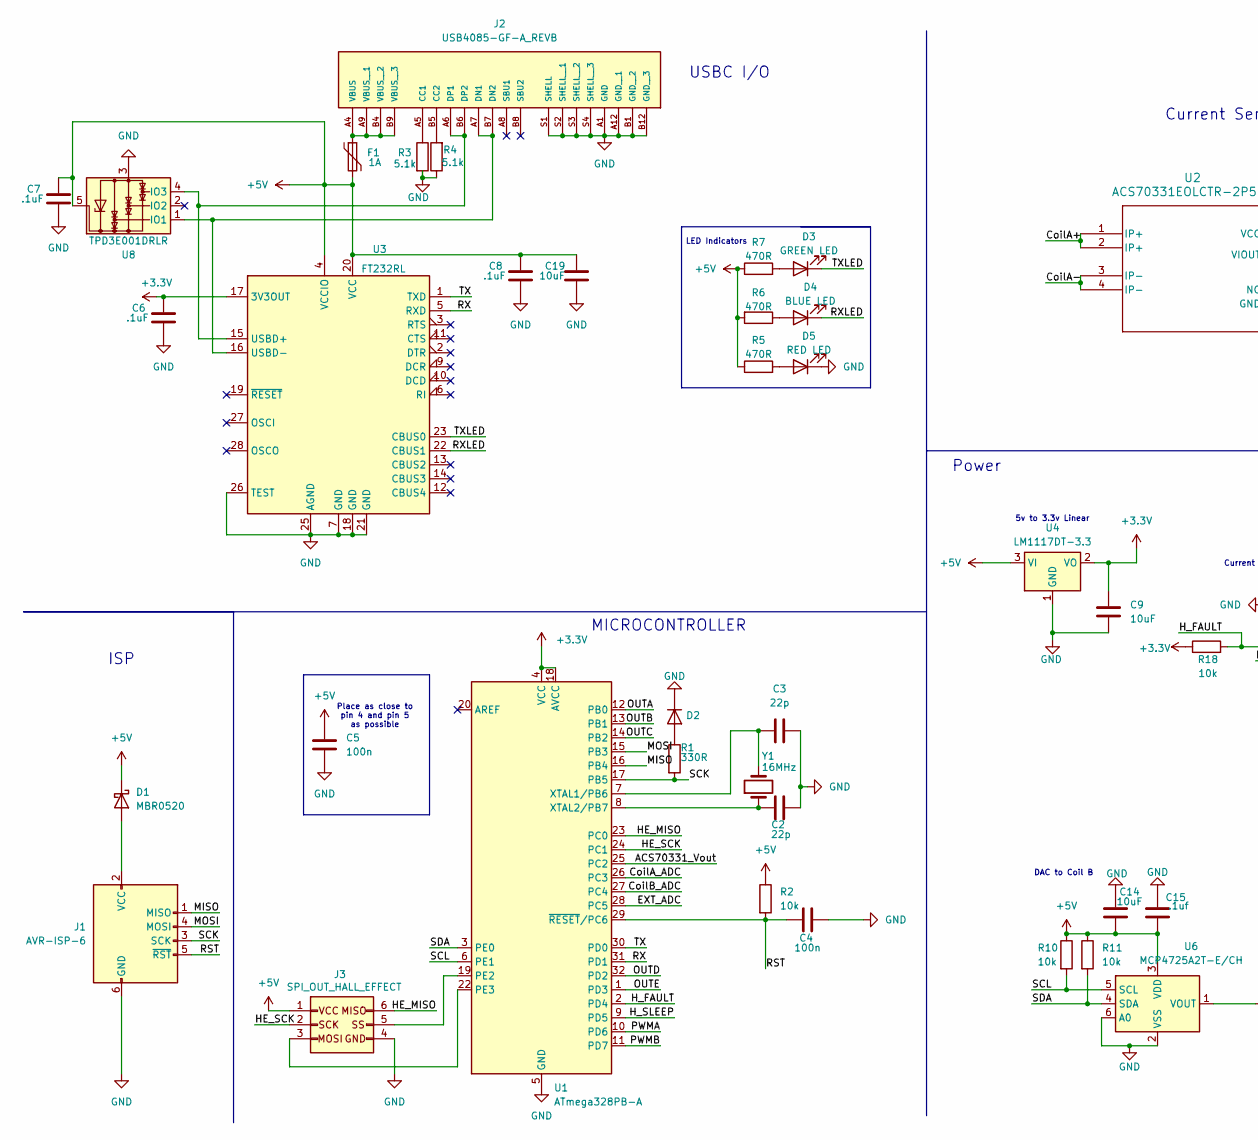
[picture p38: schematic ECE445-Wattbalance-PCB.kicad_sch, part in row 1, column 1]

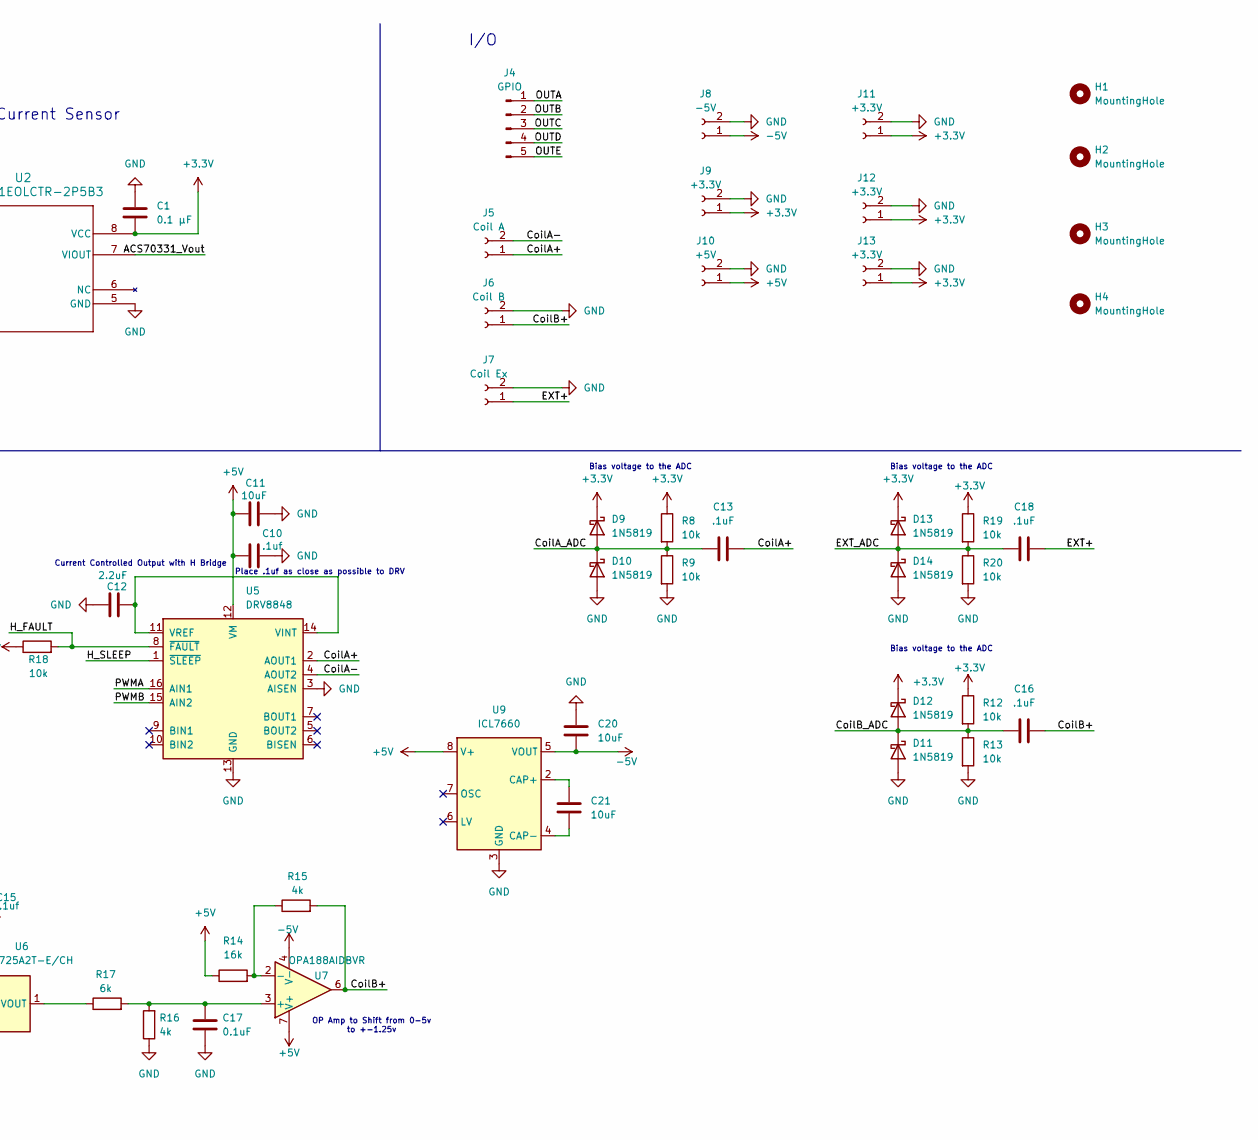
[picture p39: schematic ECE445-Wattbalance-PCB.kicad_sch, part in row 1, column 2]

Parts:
C1: 0.1 µF; C_0805_2012Metric_Pad1.18x1.45mm_HandSolder
C2, C3: 22p; C_0805_2012Metric_Pad1.18x1.45mm_HandSolder
C4, C5: 100n; C_0805_2012Metric_Pad1.18x1.45mm_HandSolder
C6, C7, C8, C13, C16, C18: .1uF; C_0805_2012Metric_Pad1.18x1.45mm_HandSolder
C9, C11, C14, C19, C20, C21: 10uF; C_0805_2012Metric_Pad1.18x1.45mm_HandSolder
C10, C15: .1uf; C_0805_2012Metric_Pad1.18x1.45mm_HandSolder
C12: 2.2uF; C_0805_2012Metric_Pad1.18x1.45mm_HandSolder
C17: 0.1uF; C_0805_2012Metric_Pad1.18x1.45mm_HandSolder
D1: MBR0520; D_SOD-123
D2: D; D_SOD-123
D3: GREEN LED; LED_D5.0mm
D4: BLUE LED; LED_D5.0mm
D5: RED LED; LED_D5.0mm
D9, D10, D11, D12, D13, D14: 1N5819; D_DO-41_SOD81_P7.62mm_Horizontal
F1: 1A; Fuse_Littelfuse-LVR100
H1, H2, H3, H4: MountingHole; MountingHole_3.2mm_M3
J1: AVR-ISP-6; IDC-Header_2x03_P2.54mm_Vertical
J2: USB4085-GF-A_REVB; GCT_USB4085-GF-A_REVB; PARTREV B
J3: SPI_OUT_HALL_EFFECT; IDC-Header_2x03_P2.54mm_Vertical
J4: GPIO; PinHeader_1x05_P2.54mm_Vertical
J5: Coil A; Molex_KK-254_AE-6410-02A_1x02_P2.54mm_Vertical
J6: Coil B; Molex_KK-254_AE-6410-02A_1x02_P2.54mm_Vertical
J7: Coil Ex; Molex_KK-254_AE-6410-02A_1x02_P2.54mm_Vertical
J8: -5V; Molex_KK-254_AE-6410-02A_1x02_P2.54mm_Vertical
J9, J11, J12, J13: +3.3V; Molex_KK-254_AE-6410-02A_1x02_P2.54mm_Vertical
J10: +5V; Molex_KK-254_AE-6410-02A_1x02_P2.54mm_Vertical
R1: 330R; R_0805_2012Metric_Pad1.20x1.40mm_HandSolder
R2, R8, R9, R10, R11, R12, R13, R18, R19, R20: 10k; R_0805_2012Metric_Pad1.20x1.40mm_HandSolder
R3, R4: 5.1k; R_0805_2012Metric_Pad1.20x1.40mm_HandSolder
R5, R6, R7: 470R; R_0805_2012Metric_Pad1.20x1.40mm_HandSolder
R14: 16k; R_0805_2012Metric_Pad1.20x1.40mm_HandSolder
R15, R16: 4k; R_0805_2012Metric_Pad1.20x1.40mm_HandSolder
R17: 6k; R_0805_2012Metric_Pad1.20x1.40mm_HandSolder
U1: ATmega328PB-A; TQFP-32_7x7mm_P0.8mm
U2: ACS70331EOLCTR-2P5B3; SOIC-8_5.23x5.23mm_P1.27mm
U3: FT232RL; SSOP-28_5.3x10.2mm_P0.65mm
U4: LM1117DT-3.3; TO-252-3_TabPin2
U5: DRV8848; TSSOP-16-1EP_4.4x5mm_P0.65mm
U6: MCP4725A2T-E/CH; SOT-23-6
U7: OPA188AIDBVR; SOIC-8_3.9x4.9mm_P1.27mm
U8: TPD3E001DRLR; SOT-553
U9: ICL7660; SOIC-8_3.9x4.9mm_P1.27mm
Y1: 16MHz; Crystal_HC49-U_Vertical

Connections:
+3.3V: C1.2, C6.1, C9.1, D9.1 (K), D12.1 (K), D13.1 (K), J9.1, J11.1, J12.1, J13.1, R8.1, R12.1, R18.1, R19.1, U1.4 (VCC), U1.18 (AVCC), U2.8 (VCC), U3.17 (3V3OUT), U4.2 (VO)
+5V: C5.1, C7.1, C8.1, C10.2, C11.1, C14.1, C15.2, C19.1, D1.1 (K), F1.2, J3.1, J10.1, R2.1, R5.1, R6.2, R7.1, R10.1, R11.1, R14.1, U3.4 (VCCIO), U3.20 (VCC), U4.3 (VI), U5.12 (VM), U6.3 (VDD), U7.7 (V+), U8.5, U9.8 (V+)
-5V: C20.2, J8.1, U7.4 (V-), U9.5 (VOUT)
/ACS70331_Vout: U1.25 (PC2), U2.7 (VIOUT)
/CoilA+: C13.2, J5.1, U2.1 (IP+), U2.2 (IP+), U5.2 (AOUT1)
/CoilA-: J5.2, U2.3 (IP-), U2.4 (IP-), U5.4 (AOUT2)
/CoilA_ADC: C13.1, D9.2 (A), D10.1 (K), R8.2, R9.1, U1.26 (PC3)
/CoilB+: C16.2, J6.1, R15.2, U7.6
/CoilB_ADC: C16.1, D11.1 (K), D12.2 (A), R12.2, R13.1, U1.27 (PC4)
/EXT+: C18.2, J7.1
/EXT_ADC: C18.1, D13.2 (A), D14.1 (K), R19.2, R20.1, U1.28 (PC5)
/HE_MISO: J3.6, U1.23 (PC0)
/HE_SCK: J3.2, U1.24 (PC1)
/H_FAULT: R18.2, U1.2 (PD4), U5.8 (~FAULT)
/H_SLEEP: U1.9 (PD5), U5.1 (~SLEEP)
/MISO: J1.1 (MISO), U1.16 (PB4)
/MOSI: J1.4 (MOSI), U1.15 (PB3)
/OUTA: J4.1, U1.12 (PB0)
/OUTB: J4.2, U1.13 (PB1)
/OUTC: J4.3, U1.14 (PB2)
/OUTD: J4.4, U1.32 (PD2)
/OUTE: J4.5, U1.1 (PD3)
/PWMA: U1.10 (PD6), U5.16 (AIN1)
/PWMB: U1.11 (PD7), U5.15 (AIN2)
/RST: C4.1, J1.5 (~RST), R2.2, U1.29 (~RESET/PC6)
/RX: U1.31 (PD1), U3.5 (RXD)
/RXLED: D4.1 (K), U3.22 (CBUS1)
/SCK: J1.3 (SCK), R1.2, U1.17 (PB5)
/SCL: R10.2, U1.6 (PE1), U6.5 (SCL)
/SDA: R11.2, U1.3 (PE0), U6.4 (SDA)
/TX: U1.30 (PD0), U3.1 (TXD)
/TXLED: D3.1 (K), U3.23 (CBUS0)
GND: C1.1, C2.2, C3.2, C4.2, C5.2, C6.2, C7.2, C8.2, C9.2, C10.1, C11.2, C12.2, C14.2, C15.1, C17.2, C19.2, C20.1, D2.1 (K), D5.1 (K), D10.2 (A), D11.2 (A), D14.2 (A), J1.6 (GND), J2.A1 (GND), J2.A12 (GND__1), J2.B1 (GND__2), J2.B12 (GND__3), J2.S1 (SHELL), J2.S2 (SHELL__1), J2.S3 (SHELL__2), J2.S4 (SHELL__3), J3.4, J6.2, J7.2, J8.2, J9.2, J10.2, J11.2, J12.2, J13.2, R3.2, R4.1, R9.2, R13.2, R16.1, R20.2, U1.5 (GND), U1.21 (GND), U2.5 (GND), U3.7 (GND), U3.18 (GND), U3.21 (GND), U3.25 (AGND), U3.26 (TEST), U4.1 (GND), U5.3 (AISEN), U5.13 (GND), U5.17 (GND), U6.2 (VSS), U6.6 (A0), U8.3, U9.3 (GND)
unnamed: D1.2 (A), J1.2 (VCC)
unnamed: D2.2 (A), R1.1
unnamed: D3.2 (A), R7.2
unnamed: D4.2 (A), R6.1
unnamed: D5.2 (A), R5.2
unnamed: J2.A5 (CC1), R3.1
unnamed: J2.B5 (CC2), R4.2
unnamed: J2.A7 (DN1), J2.B7 (DN2), U3.16 (USBD-), U8.1 (IO1)
unnamed: J2.A6 (DP1), J2.B6 (DP2), U3.15 (USBD+), U8.4 (IO3)
unnamed: F1.1, J2.A4 (VBUS), J2.A9 (VBUS__1), J2.B4 (VBUS__2), J2.B9 (VBUS__3)
unnamed: J3.3, U1.22 (PE3)
unnamed: J3.5, U1.19 (PE2)
unnamed: C3.1, U1.7 (XTAL1/PB6), Y1.2
unnamed: C2.1, U1.8 (XTAL2/PB7), Y1.1
unnamed: C12.1, U5.11 (VREF), U5.14 (VINT)
unnamed: R17.1, U6.1 (VOUT)
unnamed: C17.1, R16.2, R17.2, U7.3 (+)
unnamed: R14.2, R15.1, U7.2 (-)
unnamed: C21.1, U9.2 (CAP+)
unnamed: C21.2, U9.4 (CAP-)

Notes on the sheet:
Bias voltage to the ADC
DAC to Coil B
Power
5v to 3.3v Linear
MICROCONTROLLER
USBC I/O
ISP
LED Indicators
Current Controlled Output with H Bridge
Place .1uf as close as possible to DRV
OP Amp to Shift from 0-5v to +-1.25v
Current Sensor
I/O
Place as close to pin 4 and pin 5 as possible

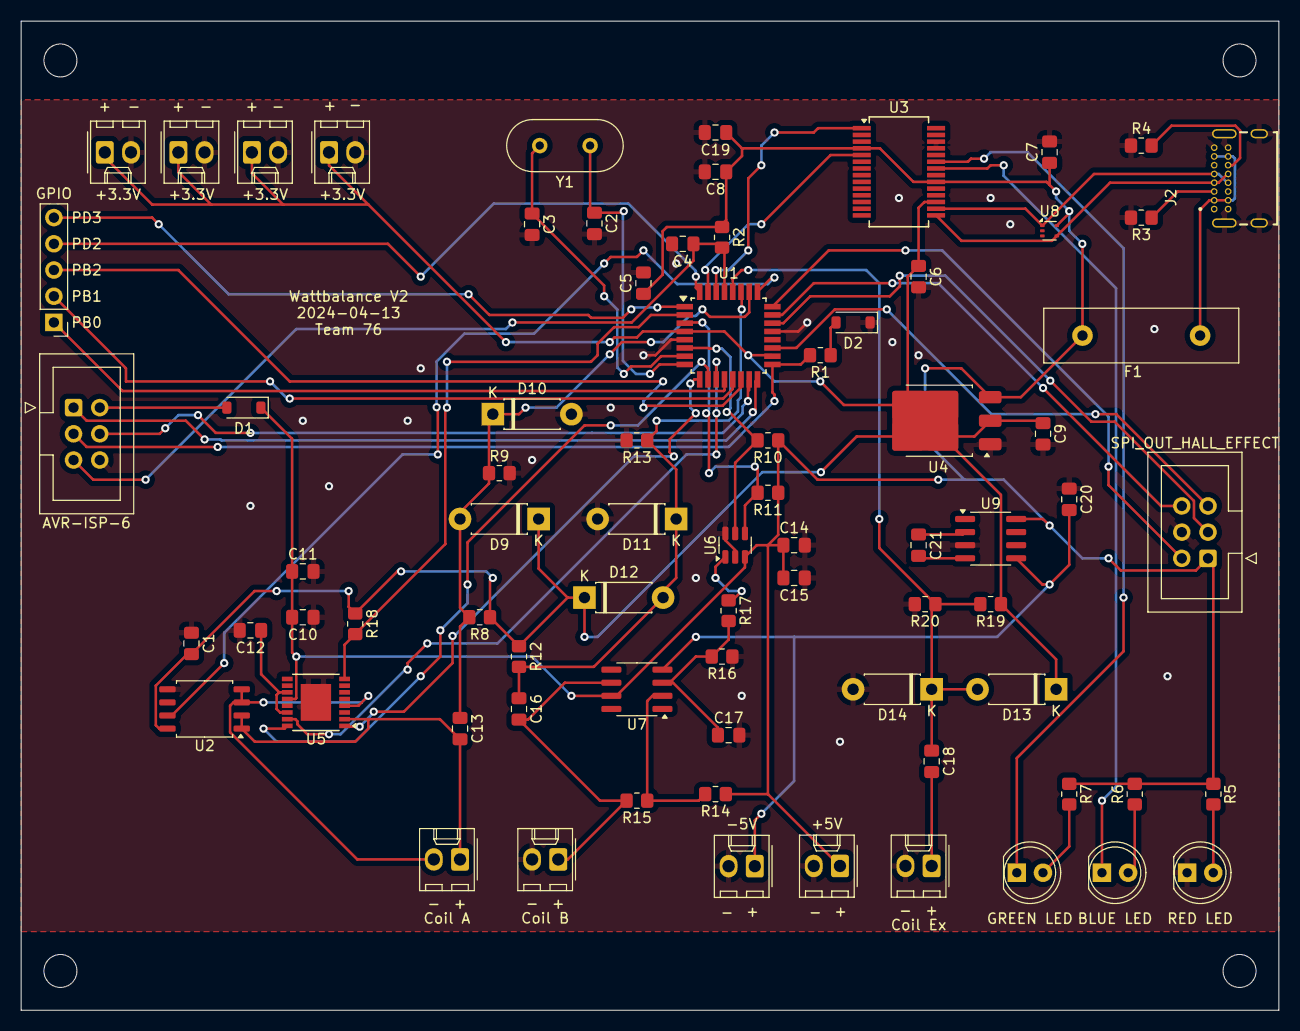
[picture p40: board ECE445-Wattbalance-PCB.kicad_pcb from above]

Board: 2 copper layers, 121.9 x 95.9 mm, 80 parts (0 on the bottom side), 53 nets.

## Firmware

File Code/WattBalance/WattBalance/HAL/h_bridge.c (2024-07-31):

#include "h_bridge.h"
#include <avr/io.h>
#include <math.h>
#include "../config.h"
#include "../timer.h"

/*-----------------------------------------------------------------
 * PWM Half Bridge Control (DRV8848)
 * Ports PD4 (H_FAULT), PD5 (H_SLEEP), PD6 (PWMA), PD7 (PWMB)
 *-----------------------------------------------------------------*/

static volatile u8 duty_cycle = 0;
static volatile u8 current_tick = 0;

void pwm_callback(){
	if (current_tick < duty_cycle) {
		PORTD |= (1 << PORTD6) | (1 << PORTD7);  // Set PD6 and PD7 high.
	} else {
		PORTD &= ~((1 << PORTD6) | (1 << PORTD7));  // Set PD6 and PD7 low.
	}
	current_tick = (current_tick + 1) % DUTY_CYCLE_LENGTH;
}

void set_pwm(u16 new_duty_cycle) {
	duty_cycle = (new_duty_cycle * DUTY_CYCLE_LENGTH) / 100; // Turn percentage into a tick
}

void init_hb(void){
	current_tick = 0; // Reset current tick value.
	
	DDRD |= (1 << PORTD6) | (1 << PORTD7); // Setup D6 and D7 for Output.
	
	DDRD  |= (1 << PORTD4);  // Enable D4 for output.
	PORTD &= ~(1 << PORTD4); // Make D4 active low.
	
	DDRD &= ~(1 << PORTD5);  // Enable PD5 as an input.
	PORTD |= (1 << PORTD5);  // Enable pull-up resistor on PD5.
	
	PORTD |= (1 << PORTD4);  // Enable chip setting sleep high.
	
}

void start_pwm(){
	current_tick = 0; // Reset current tick value.
	init_timer2(HB_TIMER, pwm_callback); // Start the timer
}

void stop_pwm(){
	stop_timer2(); // Stop the timer to stop the output
	current_tick = 0; // Reset current tick value.
	PORTD &= ~((1 << PORTD6) | (1 << PORTD7));  // Set PD6 and PD7 low.
}

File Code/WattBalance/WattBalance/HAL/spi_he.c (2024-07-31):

/*-----------------------------------------------------------------
 * Hall Effect Sensor (ERCK 05SPI 360) SPI Setup
 * Ports PE3 (MOSI), PE2 (SS), PC0 (MISO), PC1 (SCK)
 *-----------------------------------------------------------------*/
void init_spi_he(void){
	
}

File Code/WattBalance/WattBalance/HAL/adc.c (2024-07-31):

#include "adc.h"
#include <avr/io.h>
#include "../config.h"
/*-----------------------------------------------------------------
 * ADC Voltage Readings
 * Ports PC3 (Coil A), PC4 (Coil B), PC5 (Extra), PC2 (Current Sensor)
 *-----------------------------------------------------------------*/

/*
* init_adc
* This function enables ADC capabilities on the ATMega
*/
void init_adc(void) {
	ADMUX = ADC_REF_AVCC;
	ADCSRA = ADC_ENABLE | ADC_PRESCALER_128;
}

/* read_adc
 * Reads an ADC value from a specified channel.
 * Parameters: channel - ADC channel to read
 * Returns: ADC conversion result as a uint16_t
 */
u16 read_adc(u8 channel){
	ADMUX = (ADMUX & 0xF0) | (channel & 0x0F);
	ADCSRA |= (1<<ADSC);
	while (ADCSRA & (1<<ADSC));
	return ADC;
}
